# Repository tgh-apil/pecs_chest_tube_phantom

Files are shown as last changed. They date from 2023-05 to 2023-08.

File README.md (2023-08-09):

# APIL PECS/Chest Tube Phantom

 <br>

The APIL Pectoralis and Chest Tube Phantom created with a combination of 3D printed structural elements and a series of replacable echogenic gel inserts for each procedure.

The PECS inserts are ultrasoundable and a bolus of liquid can be deposited between the layers to simulate the delivery of an anesthetic agent. Additionally, the chest tube insert is made with a synthetic gel which simulates the tactile feel of human muscle with an additional fabric layer to simulate the pleural membrane.

This model was developed at the [Lynn & Arnold Irwin Advanced Perioperative Imaging Lab](https://apil.ca), Toronto General Hospital, University Health Network.

# Purchasing Information
To purchase this phantom, please email <apil@uhn.ca> and a represtative will be in touch with you with more details.

**A purchased phantom contains the following**:

1. Fully assembled APIL PECS/Chest Tube Phantom
2. 5 x fully assembled echogenic PECS inserts
3. 5 x fully assembled chest tube inserts

# Ultrasound Images
Coming soon

# Care and Maintenance

# Materials & Equipment

## Hardware

- M5x14 Pins
- M5x80 Pins
- Various M4 Screws
- Quick-turn Lock
- 8 mm ID Silicone Tubing (any durometer)
- Tube Fittings 
- Various sized clamps
- Glue gun
- Heat gun
- Nylon mesh fabric (or equivalent)

## Printing Equipment

- Polylactic Acid (PLA)
- Fused Deposition Modelling 3D printer

## Casting Equipment

- Ballistics Gel
  - Gelatin #3 from [Humimic Medical](https://humimic.com/product/gelatin-3-medical-gel-by-the-pound/)
- Graphite Powder
  - used to replicate echogenic scatter of muscle
- Slowcooker
- Two-part Platinum Cure Silicone Rubber (or equivalent)
  - Available from [Smooth-On](https://www.smooth-on.com/products/dragon-skin-30/)
- Degas Chamber (Optional)

# Assembly Instructions

### **Note:** This is a ***very*** complex phantom to manufacture involving a large investment of printer time, filament, silicone, and synthetic gel.

## Printing

This repo includes **stl** files for each printed part.  Several of the more complicated parts also have a **3mf** with support enforcers/blockers in place.  Please ntoe that the **3mf** files replicate the exact printing settings we use for production in the lab using the **Prusa MK3S** as the printer and **PLA** as the filament and may be incompatible other your 3D printers and materials.

In general, we use the following settings for *all* parts of this phantom:

<table>
    <tr>
        <td><b>Material</b></td>
        <td><b>Colour</b></td>
        <td><b>Nozzle Temp (C)</b></td>
        <td><b>Bed Temp (C)</b></td>
        <td><b>Infill (%)</b></td>
        <td><b>Perimiters (#)</b></td>
    </tr>
    <tr>
        <td>PLA</td>
        <td>White</td>
        <td>210.0</td>
        <td>60.0</td>
        <td>10.0</td>
        <td>2</td>
    </tr>
</table>

## Silicone Casting

### Silicone Shell Casting

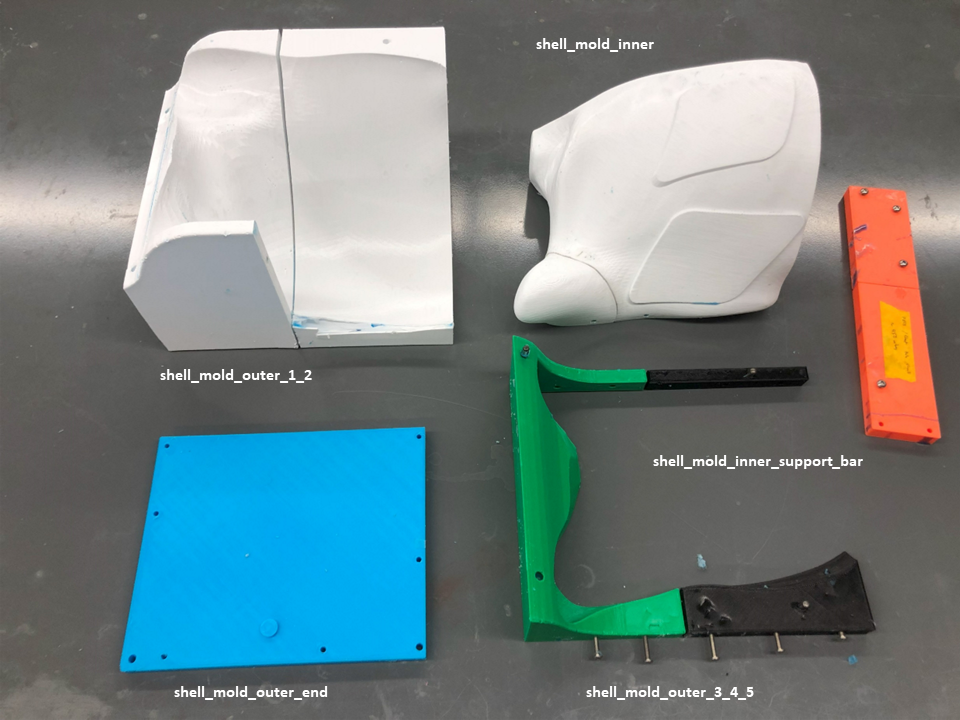
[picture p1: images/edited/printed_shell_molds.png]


**NOTE:** We are in the process of updating this mold assembly to make this process much easier.  Currently, this process is extremely difficult.

1. Print all components in the directory */shell_mold_parts/shell_mold_parts/* using the printing settings outlined above.
2. Mix **750 g** of silicone according to manufacturers instructions.
    - Degassing the silicone is encoraged, but optional.
    - Adding colourant to silicone is optional.
3. Pour 3/4 of silicone into the assembled outer mold.
4. Insert the assembled inner mold.
5. Insert necessary M4 bolts around the top rim of mold.
6. Carefully pour remaining 1/4 silicone into the empty spaces of the mold.
7. Allow silicone to cure according to manufacturer's instructions.
8. Carefully disassmble the mold and release the silicone.
   - **NOTE:** This step can be very difficult.  Procede with caution and patience to avoid damaging the silicone shell.

### Silicone PECS and Chest Tube Inserts Molds Casting

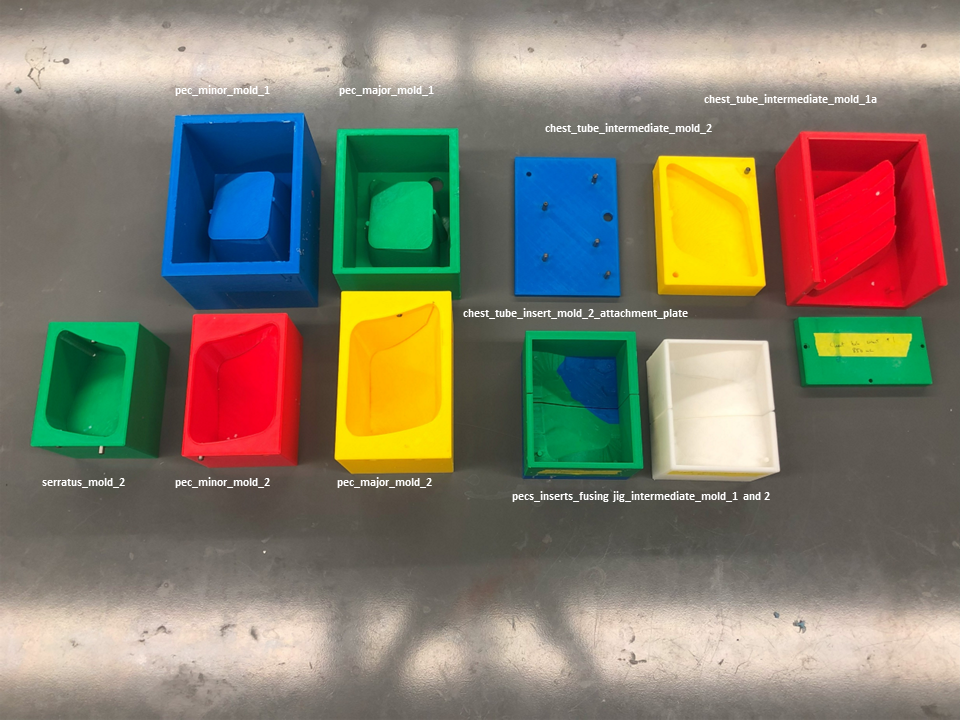
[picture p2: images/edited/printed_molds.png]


1. Print all components in the directory */pecs_chest_tube_inserts_molds/* using the printing settings outlined above.
2. Mix **4000 g** of silicone according to manufacturers instructions.
   1. Cast **1000 g** of mixed silicone into serratus_mold_1 and serratus_mold_2.
   2. Cast **1800 g** of mixed silicone into pecs_minor_mold_1 and pecs_minor_mold_2.
   3. Cast **1200 g** of mixed silicone into pecs_major_mold_1 and pecs_major_mold_2.
3. Assemble chest_tube_intermediate_mold_1a and chest_tube_intermediate_mold_1b using M4 bolts.
4. Mix **1200 g** of silicone according to manufacturers instructions and cast into assembled chest_tube_intermediate_mold_1 and chest_tube_intermediate_mold_2.
5. Allow silicone to cure according to manufacturer's instructions and de-mold silicone molds.

### Silicone PECS Fusion Jig Molds Casting
1. Print all components in the directory */pecs_chest_tube_inserts_molds/pecs_fusion_jig_molds/* using the printing settings outlined above.
2. Assemble pecs_inserts_fusion_jig_intermediate_mold_1a and pecs_inserts_fusion_jig_intermediate_mold_1b using 2 * M5x14 pins.
3. Assemble pecs_inserts_fusion_jig_intermediate_mold_2a and pecs_inserts_fusion_jig_intermediate_mold_2b using 2 * M5x14 pins.
4. Mix **1000 g** of silicone according to manufacturers instructions and cast into assembled pecs_inserts_fusion_jig_intermediate_mold_1 and pecs_inserts_fusion_jig_intermediate_mold_2.
5. Allow silicone to cure according to manufacturer's instructions and de-mold silicone molds.
6. Insert 4 * M5x80 pins into silicone PECS Fusion Jig Molds.

## Ballistics Gel Casting

1. **CAUTION:** Use appropriate heat-proof gloves when working with liquefied ballistic gel and/or heat gun.
2. **CAUTION:** work **only** in a very well ventilated area.  A fumehood is *highly* recommended.

### PECS Inserts Ballistics Gel Casting

1. Melt at least **100 g** gel in crockpot @ 105C - 115C (approx. 225F - 240F).
2. If the gel does not contain graphite powder, slowly add graphite powder into fully liquefied mixture until saturated.
3. Pour approximately **30 g** gel into each of serratus, pecs minor, and pecs major silicone molds from the previous step.
4. Allow gel to fully cool before removal from silicone molds.

### PECS Inserts Fusion

1. Demold gel from serratus, pecs minor, and pecs major molds.
2. Stack each gel layer.
3. Insert stacked gel layers into Fusion Chamber and sandwich between both chamber parts.
4. Set heat gun to **350C** and work your way around the perimiter of stacked gel layers until no gaps are visible.
5. Remove fused insert from jig.  Cut the top-left corner from the insert.  This will create a drain for injected fluids.

### Chest-Tube Inserts Ballistics Gel Casting

1. Melt at least **80 g** gel in crockpot @ 105C - 115C (approx. 225F - 240F).
2. If the gel does not contain graphite powder, slowly add graphite powder into fully liquefied mixture until saturated.
3. Cut-out a rhomboid of nylon mesh approximately the size of the bottom of chest-tube mold.
4. Insert the nylon mesh into the bottom of the silicone chest-tube mold
5. Pour approximately **70 g** gel into silicone chest-tube mold from the previous step.
6. Allow gel to fully cool before removal from silicone molds.

## Phantom Assembly

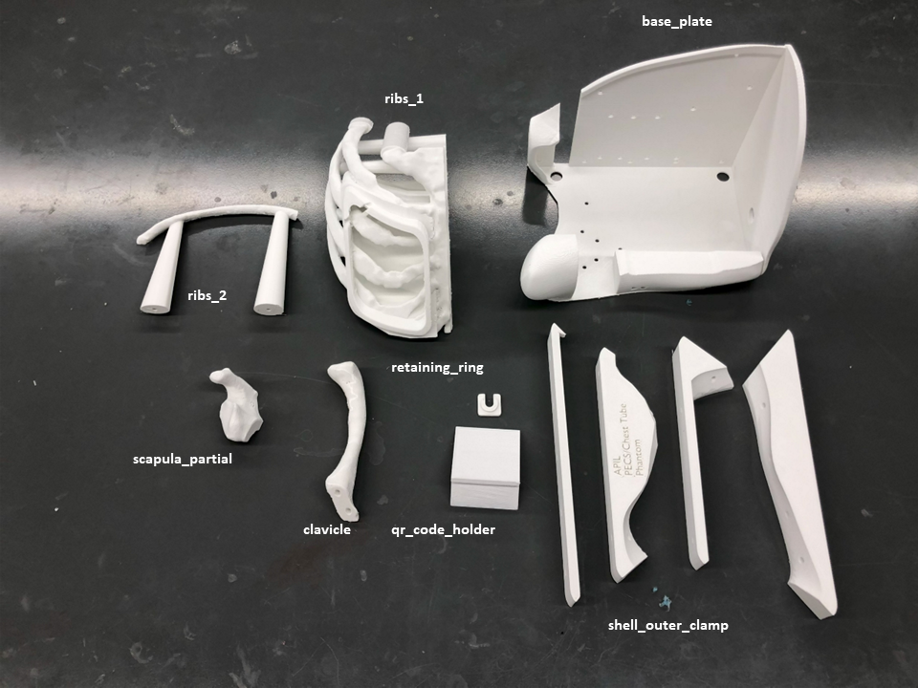
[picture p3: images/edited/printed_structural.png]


1. Print all components in the directory */bones/* and */structural_parts/* directories using the printing settings outlined above.
2. Remove all support from printed pieces
3. . Attach scapula_partial and clavicle to back_plate with M4x8 bolts.
4. Cut one end of tube fitting and insert into ribs_1 hole (underneath the PECS insert frame).  Attach with hot glue.
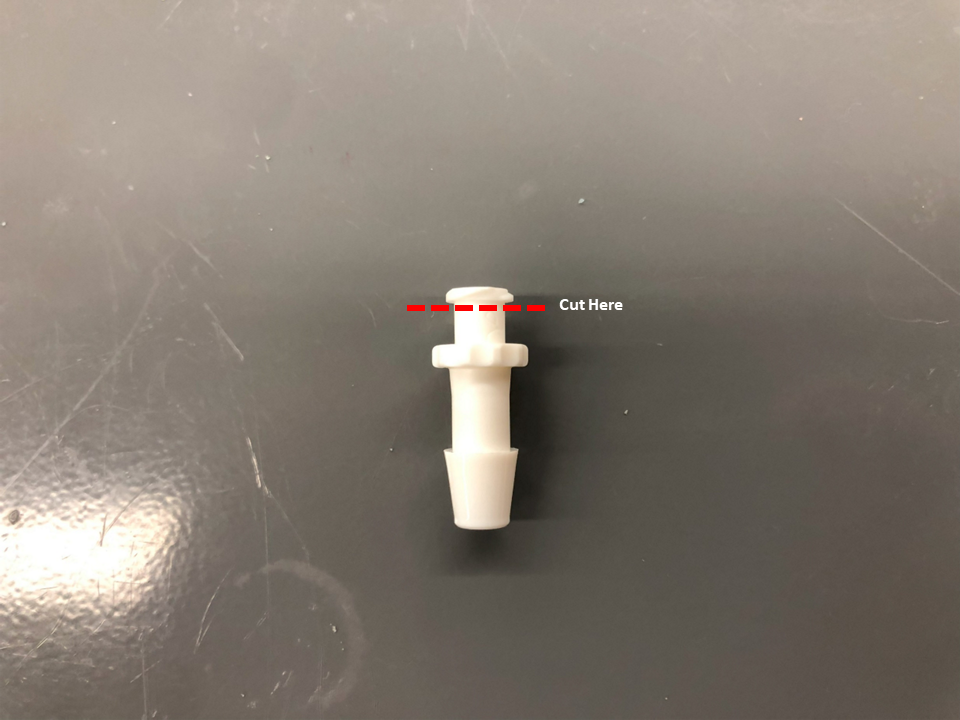
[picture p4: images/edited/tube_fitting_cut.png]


5. Attach 125 mm long silicone tubing to tube fitting.
6. Attach a second tube fitting through hole of back_plate and secure with retaining_plate and hot_glue.  Attach the silicone tubing from step #3 to this tube fitting.

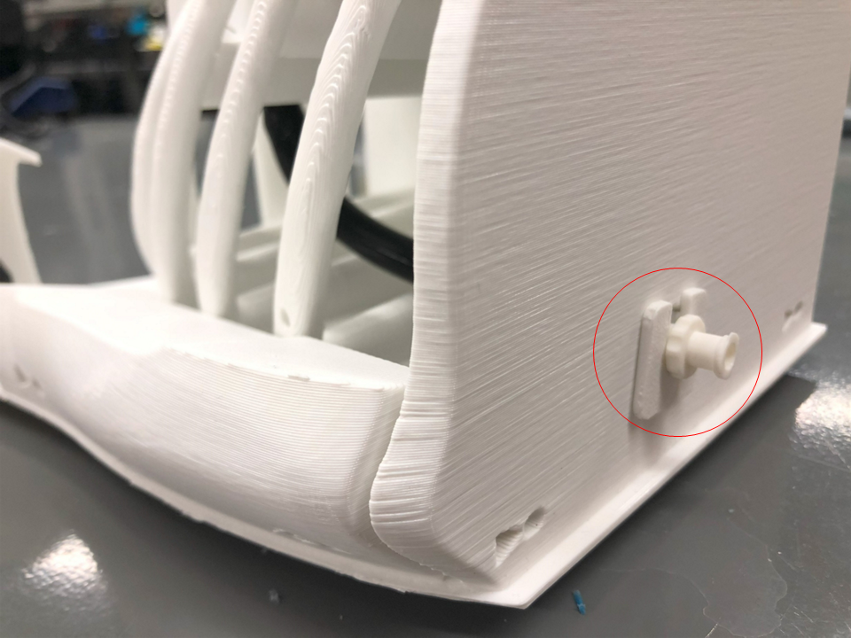
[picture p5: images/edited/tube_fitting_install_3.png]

7. Attach ribs_1 and ribs_2 to back_plate with M4x8 bolts
8. Pull silicone shell over assembled structural elements.
9.  Attach all shell_outer_clamp parts around silicone shell and secure with M4 bolts.

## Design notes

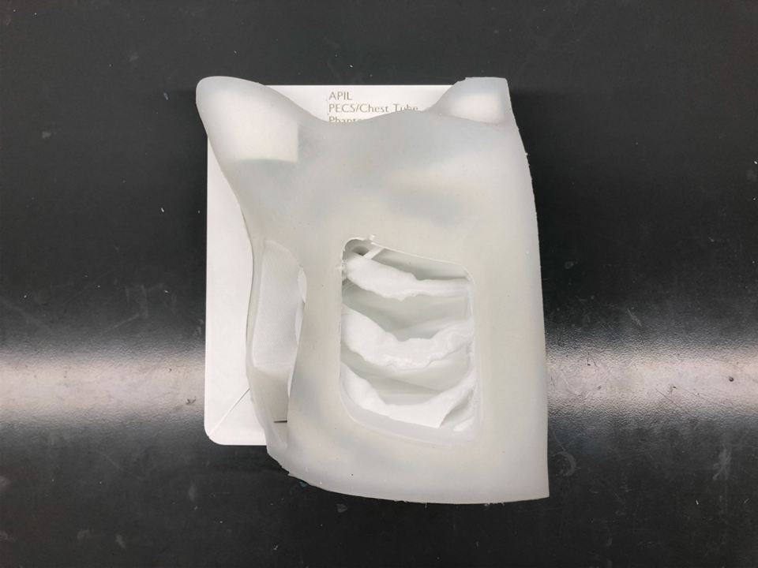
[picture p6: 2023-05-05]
images/edited/pecs_chest_tube_3.png

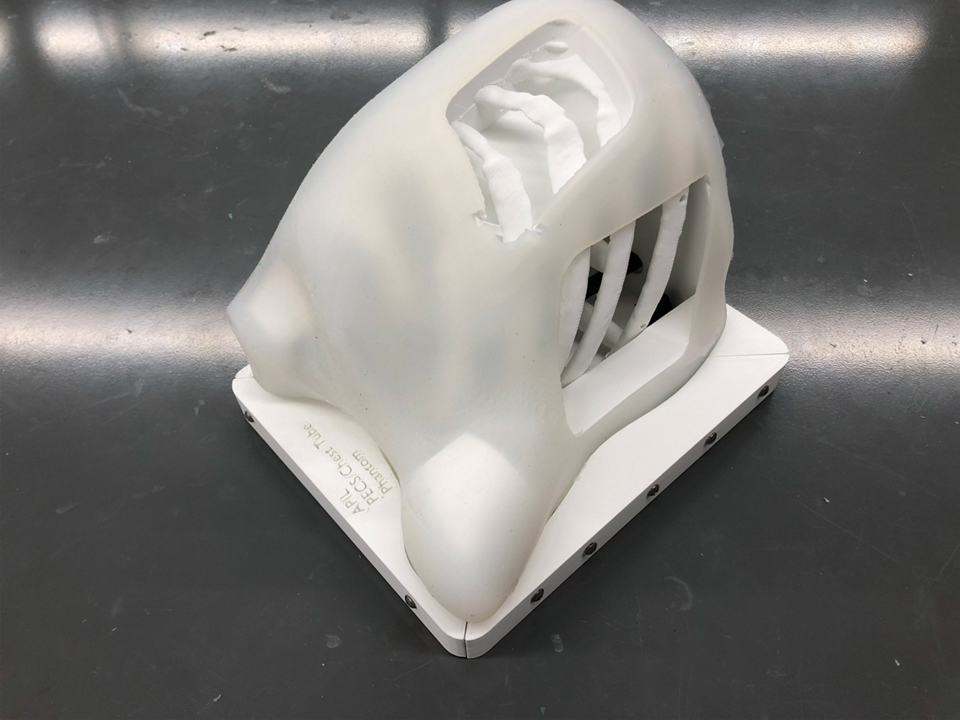
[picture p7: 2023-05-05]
images/edited/pecs_chest_tube_2.png

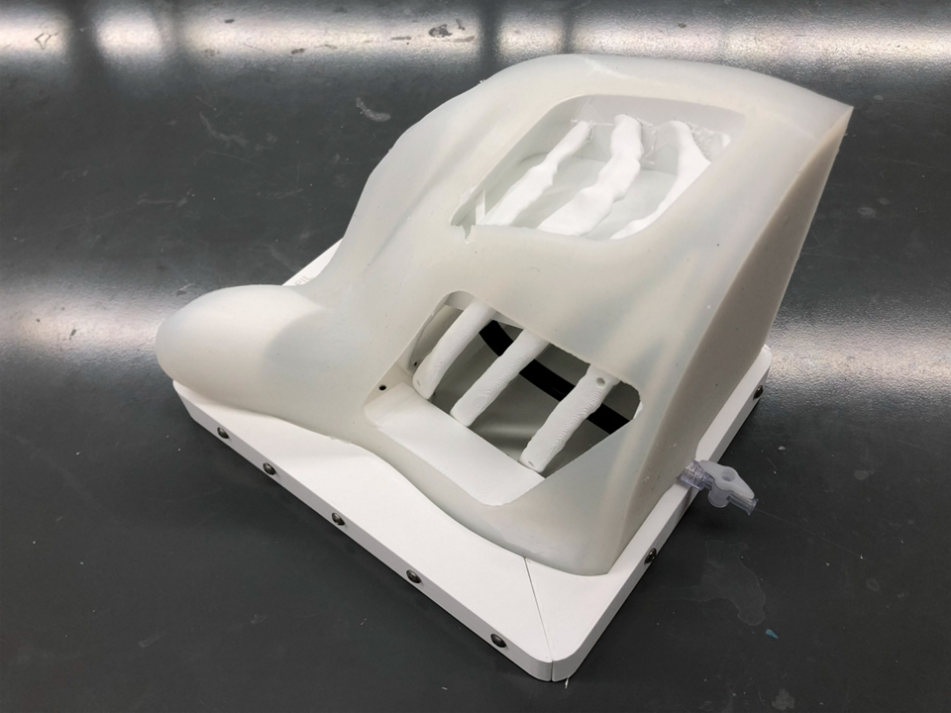
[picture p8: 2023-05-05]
images/edited/pecs_chest_tube_1.png

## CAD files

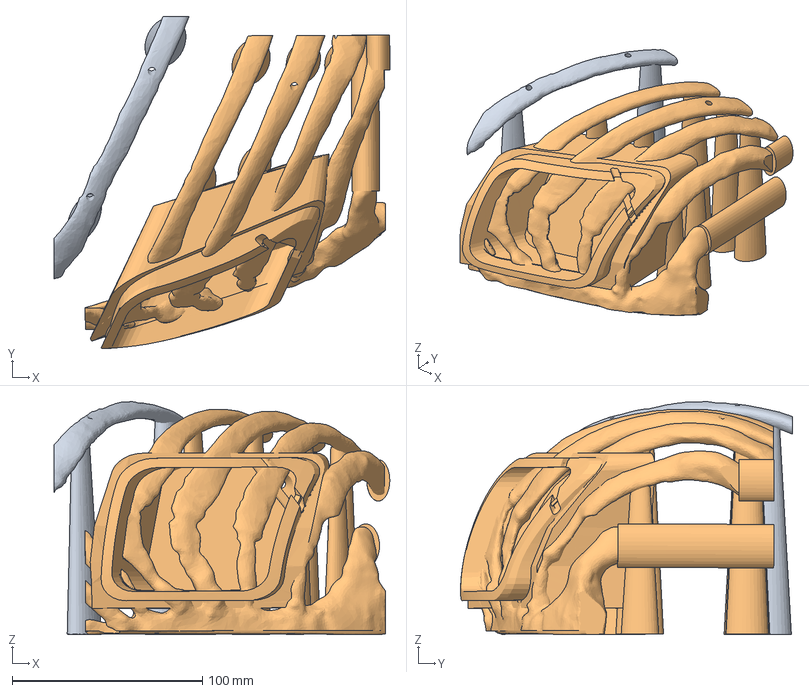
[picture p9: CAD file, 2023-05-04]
bones/ribs_supported_setup.3mf
176.5 x 174.5 x 122.5 mm
ribs_sca_2023_2.stl
ribs_sca_2023_1.stl

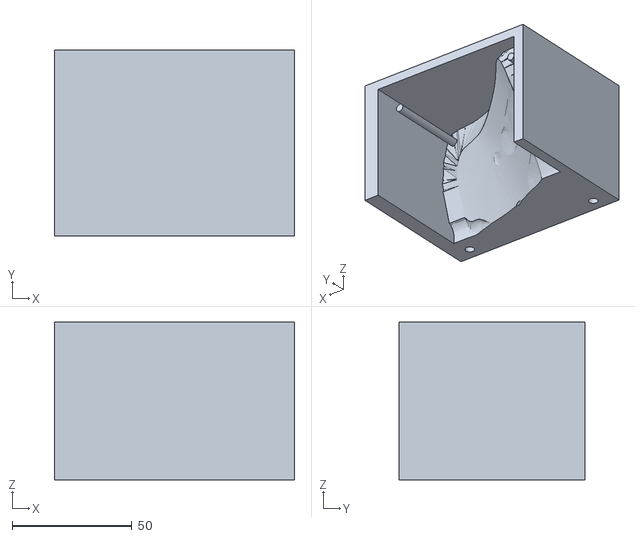
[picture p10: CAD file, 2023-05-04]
pecs_chest_tube_insert_molds/pecs_fusion_jig_molds/pecs_inserts_fusing_jig_intermediate_mold_1a.stl
100.4 x 78.0 x 66.1

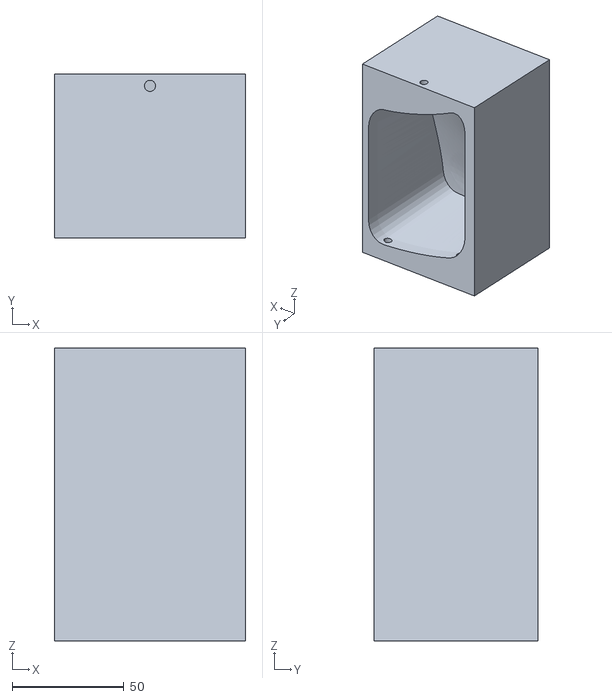
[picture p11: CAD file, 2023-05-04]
pecs_chest_tube_insert_molds/pecs_major_mold_2.stl
85.6 x 73.5 x 131.1

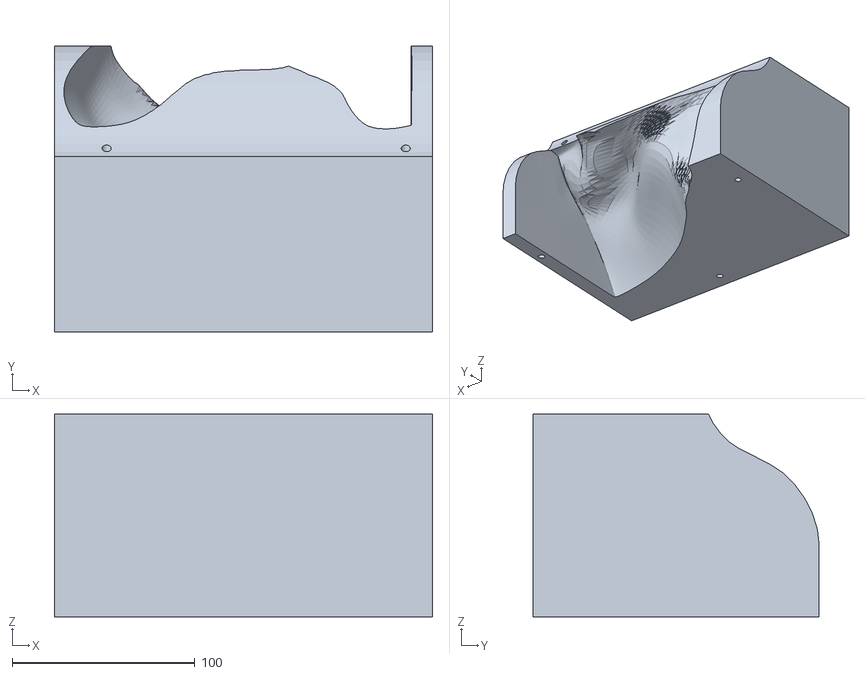
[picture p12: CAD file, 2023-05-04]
structural_parts/shell_mold_parts/shell_mold_outer_1.stl
207.0 x 156.8 x 111.1

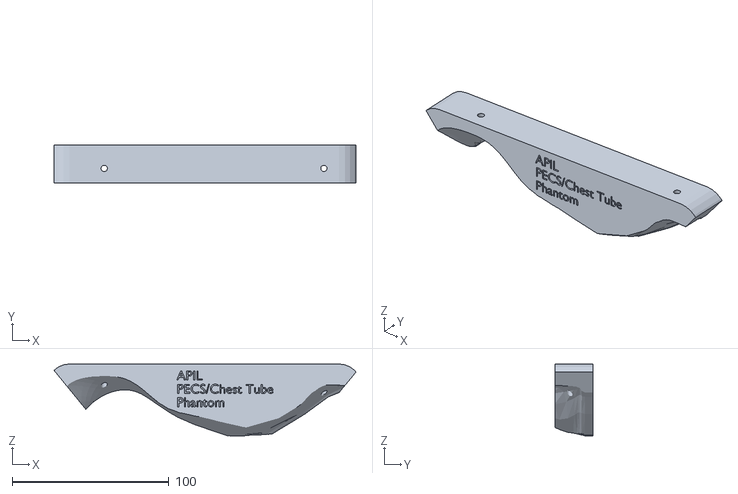
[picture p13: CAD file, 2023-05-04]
structural_parts/shell_outer_clamp_1.stl
192.5 x 24.2 x 45.8

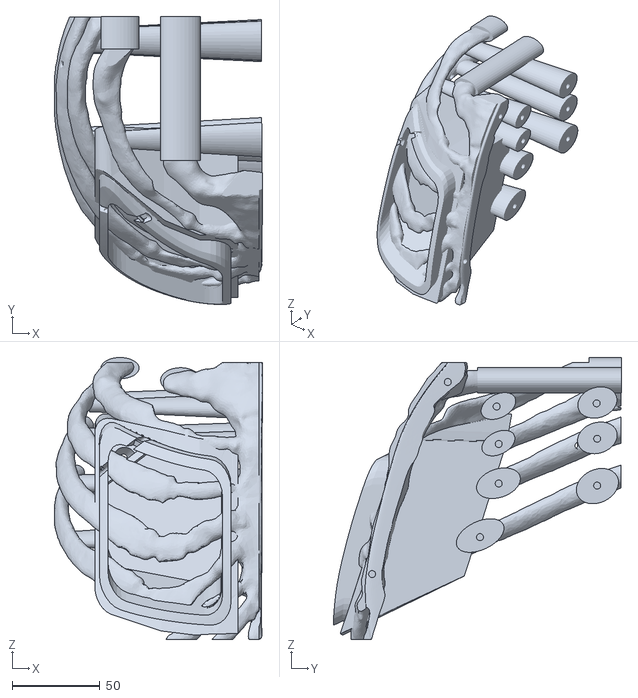
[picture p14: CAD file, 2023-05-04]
bones/ribs_1.stl
118.8 x 164.2 x 160.7

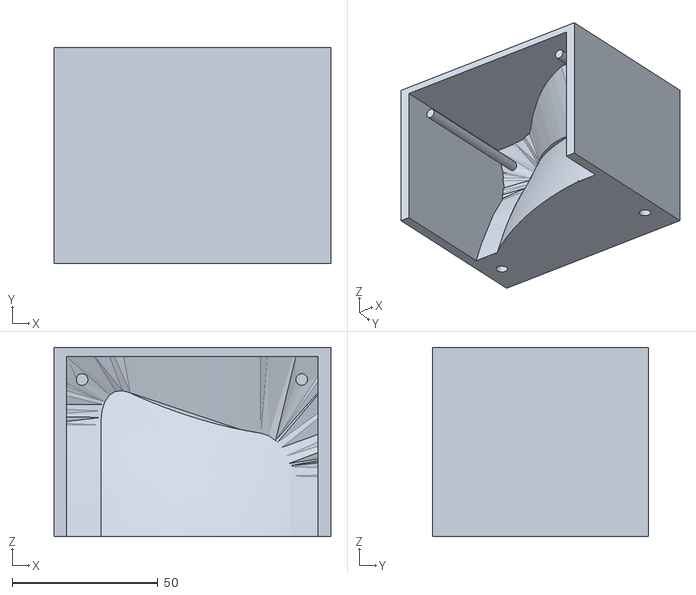
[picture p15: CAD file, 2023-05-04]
pecs_chest_tube_insert_molds/pecs_fusion_jig_molds/pecs_inserts_fusing_jig_intermediate_mold_2a.stl
95.1 x 74.2 x 65.0

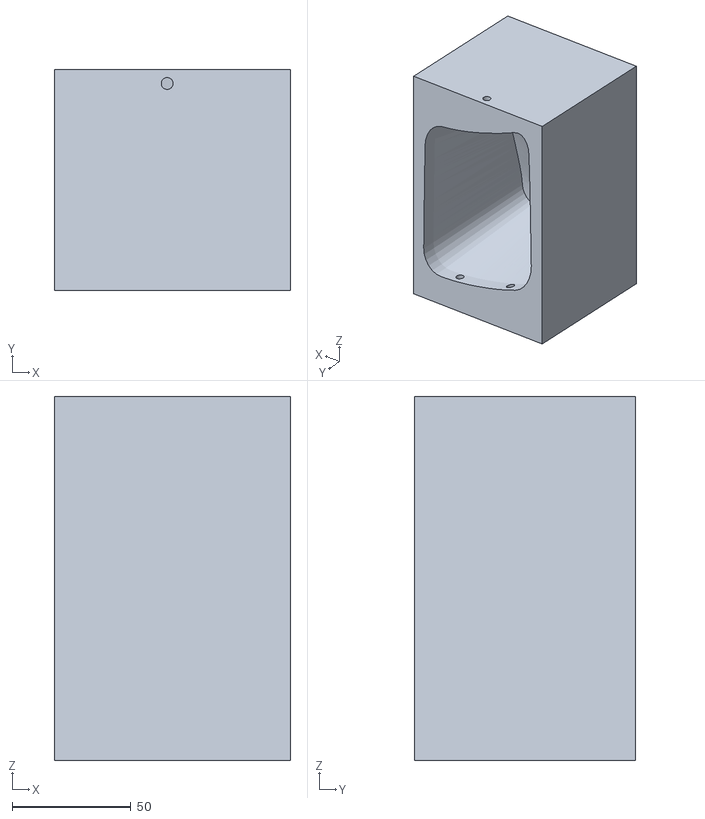
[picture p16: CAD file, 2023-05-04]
pecs_chest_tube_insert_molds/pecs_minor_mold_2.stl
99.5 x 93.2 x 153.3

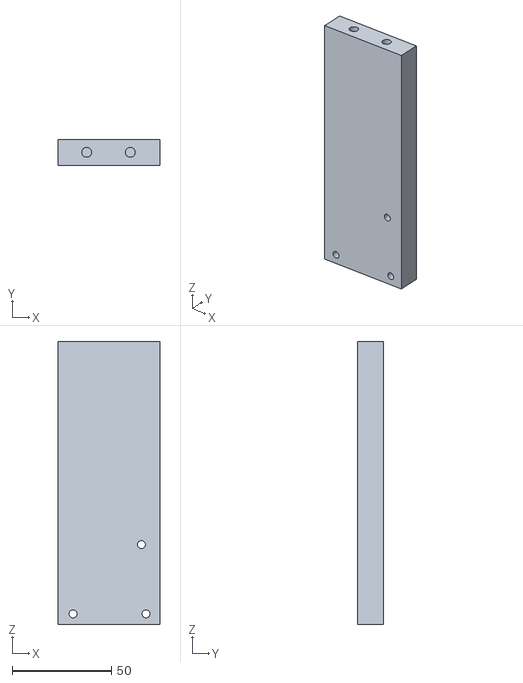
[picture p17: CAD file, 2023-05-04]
structural_parts/shell_mold_parts/shell_mold_inner_support_bar_2.stl
51.3 x 12.9 x 142.4

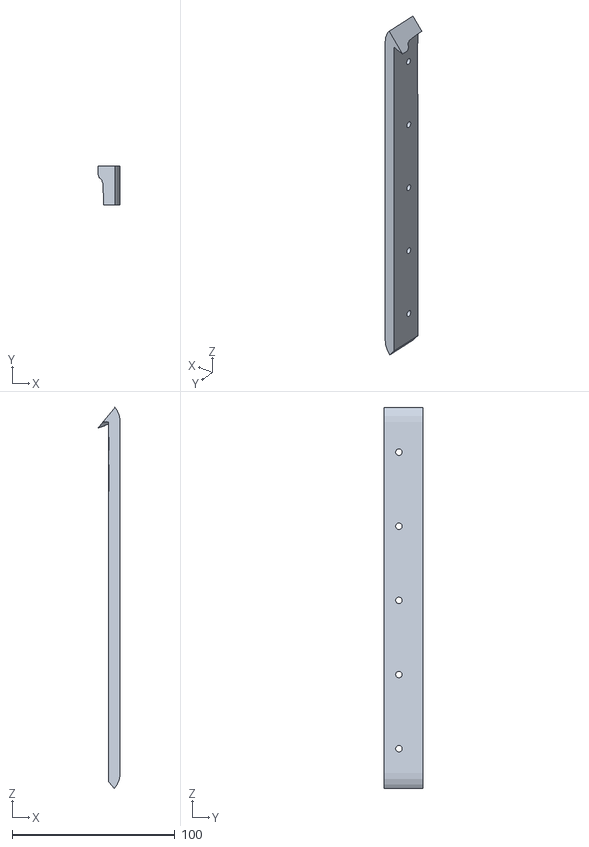
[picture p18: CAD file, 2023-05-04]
structural_parts/shell_outer_clamp_2.stl
13.8 x 24.2 x 234.3

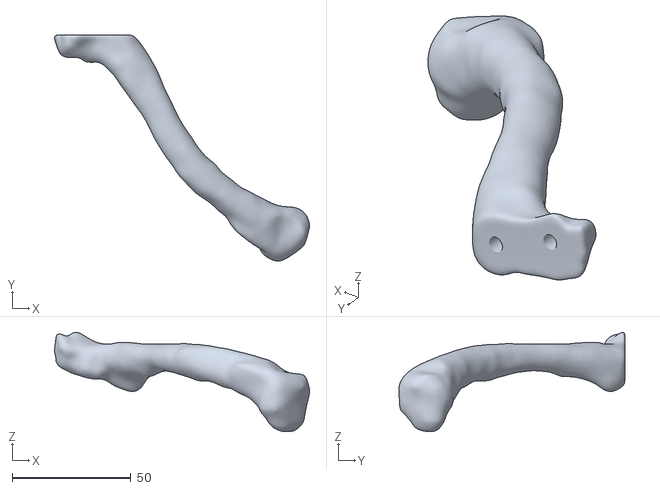
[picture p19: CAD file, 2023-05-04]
bones/clavicle.stl
107.3 x 95.2 x 41.8

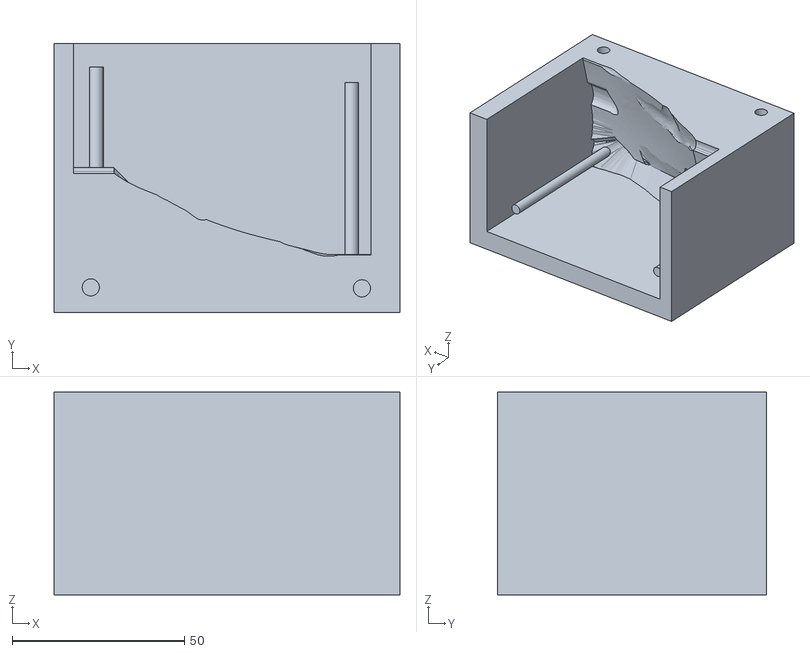
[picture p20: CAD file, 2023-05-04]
pecs_chest_tube_insert_molds/pecs_fusion_jig_molds/pecs_inserts_fusing_jig_intermediate_mold_1b.stl
100.4 x 78.0 x 58.8

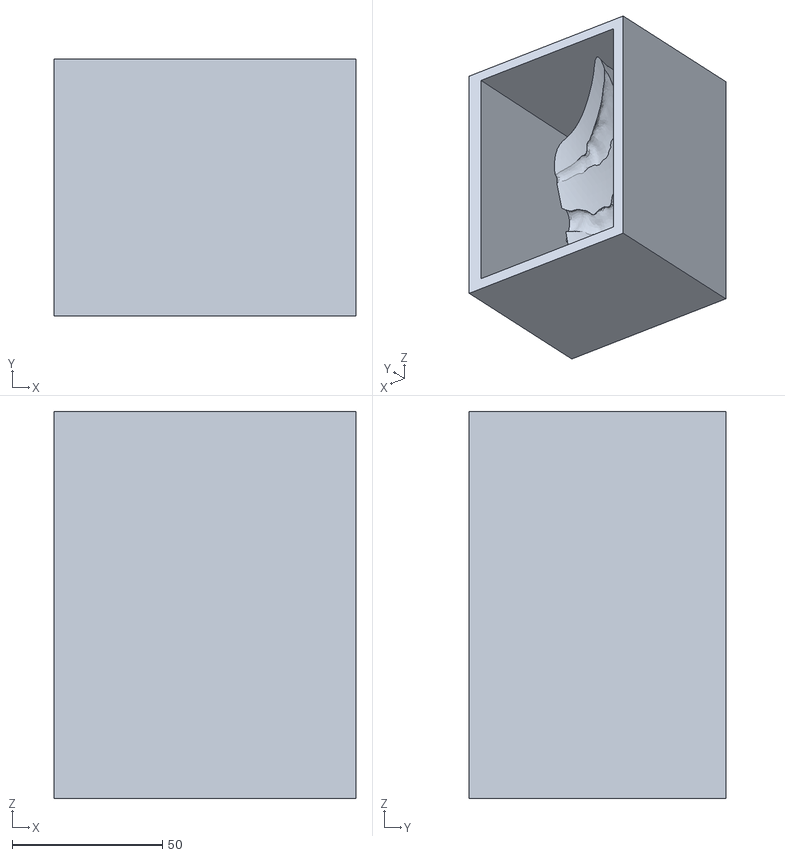
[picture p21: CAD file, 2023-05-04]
pecs_chest_tube_insert_molds/serratus_mold_1.stl
100.2 x 85.5 x 128.6

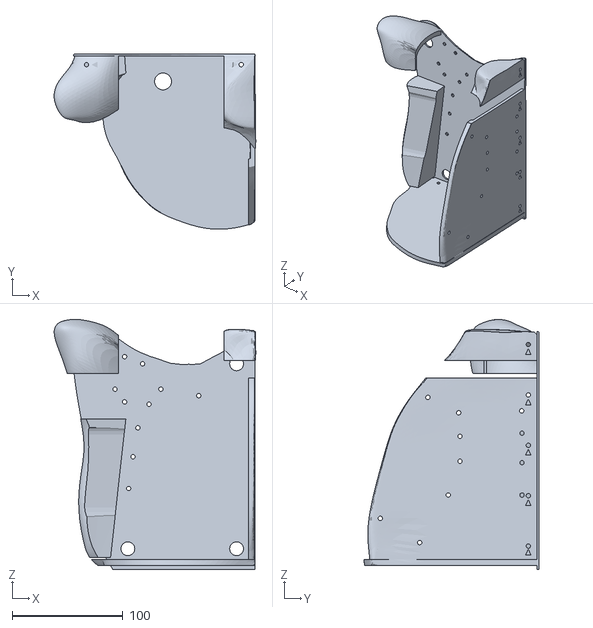
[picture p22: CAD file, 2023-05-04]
structural_parts/back_plate.stl
182.4 x 158.8 x 226.2

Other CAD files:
structural_parts/shell_mold_parts/shell_mold_outer_5.stl
bones/ribs_2.stl
pecs_chest_tube_insert_molds/chest_tube_insert_intermedaite_mold_1b.stl
pecs_chest_tube_insert_molds/pecs_fusion_jig_molds/pecs_inserts_fusing_jig_intermediate_mold_2b.stl
bones/scapula_partial.stl
pecs_chest_tube_insert_molds/chest_tube_insert_intermedaite_mold_1a.stl
pecs_chest_tube_insert_molds/chest_tube_insert_intermediate_mold_2.stl
pecs_chest_tube_insert_molds/chest_tube_insert_mold_2_attachment_plate.stl
pecs_chest_tube_insert_molds/pecs_major_mold_1.stl
pecs_chest_tube_insert_molds/pecs_minor_mold_1.stl
pecs_chest_tube_insert_molds/serratus_mold_2.stl
structural_parts/back_plate_supported_setup.3mf
structural_parts/qr_code_holder.stl
structural_parts/shell_mold_parts/shell_mold_inner.stl
structural_parts/shell_mold_parts/shell_mold_inner_support_bar_1.stl
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

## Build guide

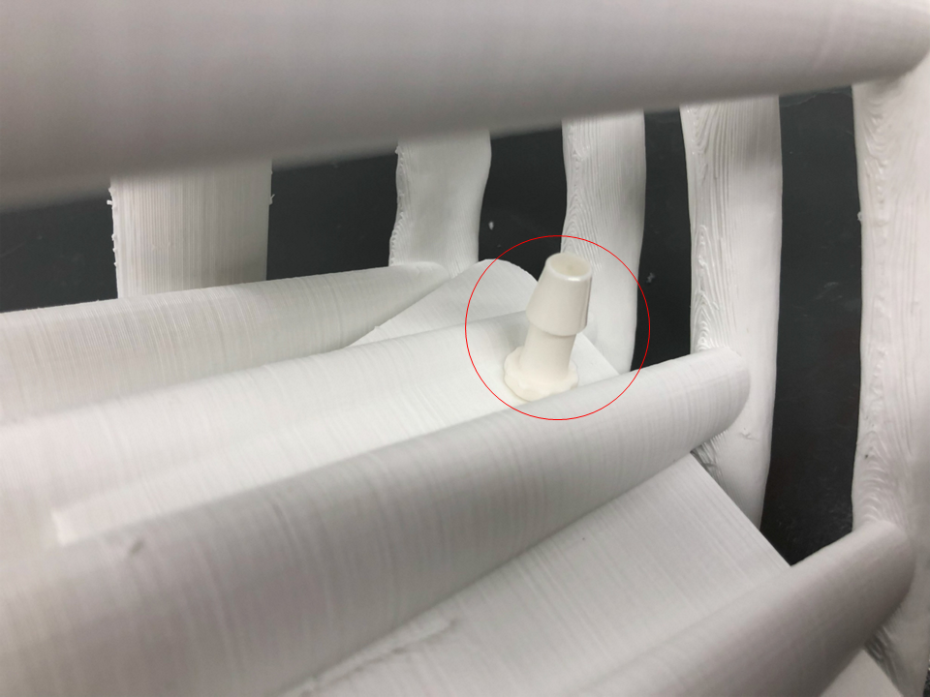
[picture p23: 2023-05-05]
images/edited/tube_fitting_install_1.png
